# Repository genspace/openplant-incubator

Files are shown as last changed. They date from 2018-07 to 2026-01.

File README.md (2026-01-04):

# OpenPlant Incubator

The code in this repository is open sourced and provides tools to develop a plant incubator.We hope this repository can be used as a model to inspire similar work among other research teams.

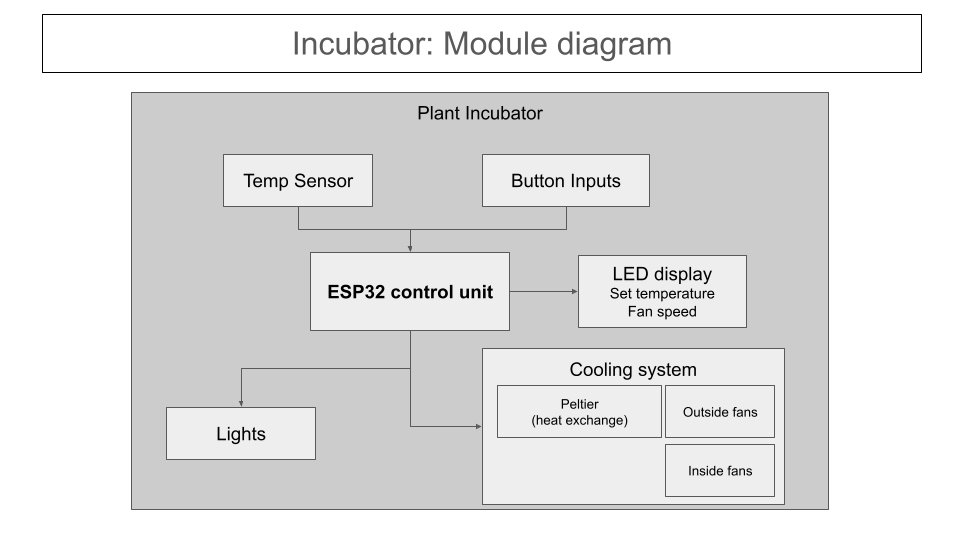
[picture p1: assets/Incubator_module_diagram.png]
Software Schematic


ToDo: Update this https://trello.com/b/W0jccEJs/welcome-to-the-project

Complete block diagram is saved in the genspace/openplant google drive. See `Incubator functional block diagram`

Please feel free to get in touch with the team.

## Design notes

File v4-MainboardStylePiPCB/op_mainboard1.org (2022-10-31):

* Task list [2/2]
- [X] lookup size limitations JLCPCB -- it seems up to 200mm x 200mm would be good
- [X] Schematic [3/3]
  - [X] mosfets
  - [X] I2C
  - [X] ATX
- [X] PCB tasks [12/12]
  - [X] copy shape from PiOnlyPCB V2
  - [X] footprints for 12 pin 3.81mm connectors
  - [X] ATX power distribution
  - [X] ATX power-on switch
  - [X] mosfets
  - [X] I2C
  - no additional copy of RPi header
  - [X] multiple mounting holes with keepouts
  - [X] silk screen additional labels
  - [X] silk screen references
  - [X] edge cuts
  - [X] Open Plant logo / label
  - [X] Flip over RPi connector

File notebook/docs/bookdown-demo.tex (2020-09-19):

\documentclass[]{book}
\usepackage{lmodern}
\usepackage{amssymb,amsmath}
\usepackage{ifxetex,ifluatex}
\usepackage{fixltx2e} % provides \textsubscript
\ifnum 0\ifxetex 1\fi\ifluatex 1\fi=0 % if pdftex
  \usepackage[T1]{fontenc}
  \usepackage[utf8]{inputenc}
\else % if luatex or xelatex
  \ifxetex
    \usepackage{mathspec}
  \else
    \usepackage{fontspec}
  \fi
  \defaultfontfeatures{Ligatures=TeX,Scale=MatchLowercase}
\fi
% use upquote if available, for straight quotes in verbatim environments
\IfFileExists{upquote.sty}{\usepackage{upquote}}{}
% use microtype if available
\IfFileExists{microtype.sty}{%
\usepackage{microtype}
\UseMicrotypeSet[protrusion]{basicmath} % disable protrusion for tt fonts
}{}
\usepackage{hyperref}
\hypersetup{unicode=true,
            pdftitle={A Minimal Book Example},
            pdfauthor={Yihui Xie},
            pdfborder={0 0 0},
            breaklinks=true}
\urlstyle{same}  % don't use monospace font for urls
\usepackage{natbib}
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
\newcommand{\AlertTok}[1]{\textcolor[rgb]{0.94,0.16,0.16}{#1}}
\newcommand{\AnnotationTok}[1]{\textcolor[rgb]{0.56,0.35,0.01}{\textbf{\textit{#1}}}}
\newcommand{\AttributeTok}[1]{\textcolor[rgb]{0.77,0.63,0.00}{#1}}
\newcommand{\BaseNTok}[1]{\textcolor[rgb]{0.00,0.00,0.81}{#1}}
\newcommand{\BuiltInTok}[1]{#1}
\newcommand{\CharTok}[1]{\textcolor[rgb]{0.31,0.60,0.02}{#1}}
\newcommand{\CommentTok}[1]{\textcolor[rgb]{0.56,0.35,0.01}{\textit{#1}}}
\newcommand{\CommentVarTok}[1]{\textcolor[rgb]{0.56,0.35,0.01}{\textbf{\textit{#1}}}}
\newcommand{\ConstantTok}[1]{\textcolor[rgb]{0.00,0.00,0.00}{#1}}
\newcommand{\ControlFlowTok}[1]{\textcolor[rgb]{0.13,0.29,0.53}{\textbf{#1}}}
\newcommand{\DataTypeTok}[1]{\textcolor[rgb]{0.13,0.29,0.53}{#1}}
\newcommand{\DecValTok}[1]{\textcolor[rgb]{0.00,0.00,0.81}{#1}}
\newcommand{\DocumentationTok}[1]{\textcolor[rgb]{0.56,0.35,0.01}{\textbf{\textit{#1}}}}
\newcommand{\ErrorTok}[1]{\textcolor[rgb]{0.64,0.00,0.00}{\textbf{#1}}}
\newcommand{\ExtensionTok}[1]{#1}
\newcommand{\FloatTok}[1]{\textcolor[rgb]{0.00,0.00,0.81}{#1}}
\newcommand{\FunctionTok}[1]{\textcolor[rgb]{0.00,0.00,0.00}{#1}}
\newcommand{\ImportTok}[1]{#1}
\newcommand{\InformationTok}[1]{\textcolor[rgb]{0.56,0.35,0.01}{\textbf{\textit{#1}}}}
\newcommand{\KeywordTok}[1]{\textcolor[rgb]{0.13,0.29,0.53}{\textbf{#1}}}
\newcommand{\NormalTok}[1]{#1}
\newcommand{\OperatorTok}[1]{\textcolor[rgb]{0.81,0.36,0.00}{\textbf{#1}}}
\newcommand{\OtherTok}[1]{\textcolor[rgb]{0.56,0.35,0.01}{#1}}
\newcommand{\PreprocessorTok}[1]{\textcolor[rgb]{0.56,0.35,0.01}{\textit{#1}}}
\newcommand{\RegionMarkerTok}[1]{#1}
\newcommand{\SpecialCharTok}[1]{\textcolor[rgb]{0.00,0.00,0.00}{#1}}
\newcommand{\SpecialStringTok}[1]{\textcolor[rgb]{0.31,0.60,0.02}{#1}}
\newcommand{\StringTok}[1]{\textcolor[rgb]{0.31,0.60,0.02}{#1}}
\newcommand{\VariableTok}[1]{\textcolor[rgb]{0.00,0.00,0.00}{#1}}
\newcommand{\VerbatimStringTok}[1]{\textcolor[rgb]{0.31,0.60,0.02}{#1}}
\newcommand{\WarningTok}[1]{\textcolor[rgb]{0.56,0.35,0.01}{\textbf{\textit{#1}}}}
\usepackage{longtable,booktabs}
\usepackage{graphicx,grffile}
\makeatletter
\def\maxwidth{\ifdim\Gin@nat@width>\linewidth\linewidth\else\Gin@nat@width\fi}
\def\maxheight{\ifdim\Gin@nat@height>\textheight\textheight\else\Gin@nat@height\fi}
\makeatother
% Scale images if necessary, so that they will not overflow the page
% margins by default, and it is still possible to overwrite the defaults
% using explicit options in \includegraphics[width, height, ...]{}
\setkeys{Gin}{width=\maxwidth,height=\maxheight,keepaspectratio}
\IfFileExists{parskip.sty}{%
\usepackage{parskip}
}{% else
\setlength{\parindent}{0pt}
\setlength{\parskip}{6pt plus 2pt minus 1pt}
}
\setlength{\emergencystretch}{3em}  % prevent overfull lines
\providecommand{\tightlist}{%
  \setlength{\itemsep}{0pt}\setlength{\parskip}{0pt}}
\setcounter{secnumdepth}{5}
% Redefines (sub)paragraphs to behave more like sections
\ifx\paragraph\undefined\else
\let\oldparagraph\paragraph
\renewcommand{\paragraph}[1]{\oldparagraph{#1}\mbox{}}
\fi
\ifx\subparagraph\undefined\else
\let\oldsubparagraph\subparagraph
\renewcommand{\subparagraph}[1]{\oldsubparagraph{#1}\mbox{}}
\fi

%%% Use protect on footnotes to avoid problems with footnotes in titles
\let\rmarkdownfootnote\footnote%
\def\footnote{\protect\rmarkdownfootnote}

%%% Change title format to be more compact
\usepackage{titling}

% Create subtitle command for use in maketitle
\providecommand{\subtitle}[1]{
  \posttitle{
    \begin{center}\large#1\end{center}
    }
}

\setlength{\droptitle}{-2em}

  \title{A Minimal Book Example}
    \pretitle{\vspace{\droptitle}\centering\huge}
  \posttitle{\par}
    \author{Yihui Xie}
    \preauthor{\centering\large\emph}
  \postauthor{\par}
      \predate{\centering\large\emph}
  \postdate{\par}
    \date{2019-10-19}

\usepackage{booktabs}
\usepackage{amsthm}
\makeatletter
\def\thm@space@setup{%
  \thm@preskip=8pt plus 2pt minus 4pt
  \thm@postskip=\thm@preskip
}
\makeatother

\begin{document}
\maketitle

{
\setcounter{tocdepth}{1}
\tableofcontents
}
\hypertarget{prerequisites}{%
\chapter{Prerequisites}\label{prerequisites}}

This is a \emph{sample} book written in \textbf{Markdown}. You can use anything that Pandoc's Markdown supports, e.g., a math equation \(a^2 + b^2 = c^2\).

The \textbf{bookdown} package can be installed from CRAN or Github:

\begin{Shaded}
\begin{Highlighting}[]
\KeywordTok{install.packages}\NormalTok{(}\StringTok{"bookdown"}\NormalTok{)}
\CommentTok{# or the development version}
\CommentTok{# devtools::install_github("rstudio/bookdown")}
\end{Highlighting}
\end{Shaded}

Remember each Rmd file contains one and only one chapter, and a chapter is defined by the first-level heading \texttt{\#}.

To compile this example to PDF, you need XeLaTeX. You are recommended to install TinyTeX (which includes XeLaTeX): \url{https://yihui.name/tinytex/}.

\hypertarget{general-use-cases}{%
\chapter{General Use Cases}\label{general-use-cases}}

As a plant researcher, I would like to have an incubator that can be controlled:

\begin{itemize}
\item
  Create schedule for light
\item
  Keep temperature constant
\item
  Keep humidity constant
\end{itemize}

As a plant researcher, I would like to capture periodic data about plants:

\begin{itemize}
\item
  Pictures - once a minute
\item
  Temperature - once a minute
\item
  Humidity - once a minute
\end{itemize}

As a plant researcher, I would like to have the data available in the cloud:

\begin{itemize}
\item
  Store all data on the cloud
\item
  View data in real time on a Web site
\end{itemize}

As a plant researcher, I would like to be able to interact with the incubator in the cloud:

\begin{itemize}
\item
  Receive alerts when the connection is down, or temperature is incorrect
\item
  Ability to change temperature and/or light settings via a Web interface
\end{itemize}

As a plant researcher, I would like to able to use analytics on the data that is captured from the incubator

\hypertarget{raspberry-pi}{%
\chapter{Raspberry Pi}\label{raspberry-pi}}

Flash Raspbian to an SD card.

\begin{itemize}
\item
  Download Raspbian Stretch Lite (raspberry pi operating system image) from \href{https://www.raspberrypi.org/downloads/raspbian/}{here}.
\item
  Download Etcher (a utility which helps you flash an image to an SD card) \href{https://www.balena.io/etcher/}{here}.
\item
  Flash Raspbian on a MicroSD card using Etcher.
\end{itemize}

Enable SSH server before the first boot of the Raspberry Pi.

\begin{itemize}
\item
  View the MicroSD card on your computer.
\item
  Find the ``boot'' partition. Right click and open a terminal.
\item
  Make a file (with nothing in it) called ``ssh'' (no quotes.)
\item
  Add a wpa\_supplicant.conf file (See Appendix A). Copy and paste the file contents from Appendix A
\item
  Change the hostname. (The Raspberry Pi image comprises two partitions. ``root'' and ``boot''. Boot is readable on all operating systems (if you insert the sd card into your laptop or whatever.) Root is only readable on Linux? Maybe Mac?) This can be done in the /rootfs directory. Name your raspberry pi by changing the `hostname' and `hosts'.
\end{itemize}

Boot the Raspbian OS on the Raspberry Pi

\begin{itemize}
\item
  Plug the microSD card into the Pi.
\item
  Power the raspberry pi with a suitable power adapter (or from the computer.)
\item
  Open Terminal. Find the Raspberry Pi on the network. \texttt{ping\ raspberrypi.local} - if it is working, press ctrl c to stop
\item
  Install nmap with \texttt{sudo\ apt\ install\ nmap}. Type: \texttt{sudo\ nmap\ -sP\ 192.168.1.0/24\ \textbar{}\ awk\ \textquotesingle{}/\^{}Nmap/\{ip=\$NF\}/B8:27:EB/\{print\ ip\}\textquotesingle{}} to find the ip address of the Pi.
\end{itemize}

Log into the Pi

\begin{itemize}
\item
  Type \texttt{ssh\ pi@raspberrypi.local} or \texttt{ssh\ pi@\{ip-address\}} where ip-address is the one from the command directly above. Accept the ``host key fingerprint'' which you are told to check. During this step, you are vulnerable to a man-in-the-middle attack. Let's assume that there is no one on the Wi-Fi who is trying to attack you. There are ways to avoid this security hole. (I.e. confirm the host key on the SD card after the first boot, but before you ever log in via SSH.
\item
  Enter the password ``raspberry''. You should change this.
\item
  (New and temporary fix) As per this \href{https://www.techrepublic.com/article/how-to-disable-ipv6-on-linux/}{article}, disable Internet Protocol version 6, as it does not play well with the Genspace Internet Service Provider. Run the following commands in a terminal window:
\end{itemize}

\begin{verbatim}
sudo nano /etc/sysctl.conf
# Add the following three lines to the bottom of the file:
net.ipv6.conf.all.disable_ipv6 = 1
net.ipv6.conf.default.disable_ipv6 = 1
net.ipv6.conf.lo.disable_ipv6 = 1

#Save and close the file.
#Reboot the machine.
\end{verbatim}

\begin{itemize}
\item
  Run \texttt{sudo\ apt-get\ update\ \&\&\ sudo\ apt-get\ -y\ upgrade} to update the system
\item
  run \texttt{sudo\ raspi-config}. In raspi-config turn on the camera and I2C in ``Interfacing Options''. Localization Settings → Keyboard Config → Generic 105 (accept default) → English US → English us → accept all defaults
\item
  Reboot
\item
  Load camera code onto pi.
\item
  Install the picamera library for python: \texttt{sudo\ apt-get\ install\ python3-picamera}
\item
  The code example uses an AWS s3 bucket to upload the files but you can choose whichever service you want.
\end{itemize}

AWS Uploading Notes

\begin{itemize}
\item
  Install the awscli program: \texttt{sudo\ apt-get\ install\ awscli}
\item
  Configure the awscli program: \texttt{aws\ configure}
\end{itemize}

Camera auto-start directions

To make the program start automatically on reboot, I edited the /etc/rc.local file as follows:

\begin{verbatim}
_IP=$(hostname -I) || true
if [ "$_IP" ]; then
  printf "My IP address is %s\n" "$_IP"
fi
su pi -c 'python3 /home/pi/kris_camera.py &'
exit 0
\end{verbatim}

\textbf{Fill In Code For Connecting Arduino And Serial Script}

\hypertarget{the-container}{%
\chapter{The Container}\label{the-container}}

Notes

\begin{itemize}
\tightlist
\item
  Designed for both Petri and `square dishes' - 4 dishes
\item
  29cm wide interior
\item
  35cm long interior
\item
  20cm high
\item
  Petri dishes are 9cm in diameter
\item
  Square dishes are 10.2cm on four sides, and 7.49cm high
\item
  Peltier+ device is 5+ cm both inside and outside
\end{itemize}

BRING LIST
* Duct tape
* Box corners
* Popsicle sticks
* Electrical tape
* Scissors
* Foam core (0.25 inch thick)
* Box cutter and or pocket knife

Polystyrene - 6 pieces and maybe some extra
* Bottom is longer in both directions
* Longer side is longer
* Shorter side is the same

Electronics
* List is on github
* Waldo has many items
* Kris to order lights

The picture is below. The desired measurements details are as follows:

20cm by 29cm by 35cm
If building, the bottom/top should longer in both directions. So, if the polystyrene is one inch thick, this means the bottom should be 2 inches (or 5+cm) longer in each dimension.
The longer two side panels should be 2 inches (or 5+cm) longer in just the length
The shorter two side panels should not have any additions
So
2 x (34 x 40cm)
2 x (20cm x 40cm)
2 x (20cm by 29 cm)

\hypertarget{arduino}{%
\chapter{Arduino}\label{arduino}}

The layout for the Arduino. What you need:

\begin{itemize}
\item
  Arduino (Uno)
\item
  \href{https://cdn.sparkfun.com/datasheets/Components/General/FQP30N06L.pdf}{Mosfet} x 2
\item
\end{itemize}

Check the code (incubator\_main.ino in \url{https://github.com/genspace/openplant-incubator}) for which pins on the Arduino to connect the lights and Peltier to. As of 10/12/19, the lights go to pin 4 and the Peltier goes to pin 5.

The Mosfet, I think it's the one above, or the one in the link below. You can always to a Google search on the.
\url{https://cdn.sparkfun.com/datasheets/Components/General/FQP30N06L.pdf}

The Peltier Module TEC1-12706
\url{https://www.electron.com/media/389/datasheet-601-017.pdf?\&key=ZGpmIyQwNUZfMzg5}

Wire the Temperature/Humidity sensor (SHT31) according to this diagram:

Fan Wiring:
We don't need to wire Sense or Control because we leave the fans always on.
\url{https://allpinouts.org/pinouts/connectors/motherboards/motherboard-cpu-4-pin-fan/}

Real Time Clock wiring
GND to GND on your board
VCC to the logic level power of your board (on classic Arduinos \& Metros use 5V, on 3.3V devices use 3.3V)
SDA to the SDA i2c data pin (A4)
SCL to the SCL i2c clock pin (A5)

\url{https://learn.adafruit.com/adafruit-pcf8523-real-time-clock/rtc-with-arduino}
\url{https://learn.adafruit.com/adafruit-metro-mini/pinouts}
Set the time by running the example script: \url{https://github.com/adafruit/RTClib/blob/master/examples/pcf8523/pcf8523.ino}

Power Supply goes into the rails -- black into one, and red into another..

Uploading code into an Arduino (in our case the Adafruit Metro Mini, which is equivalent to the Arduino Uno.)

Install the Arduino IDE

Open the IDE. (This gives a blank document. Just ``setup()'' and ``loop()'' functions

Select the board. (In tools?)

Select the serial device which you're using. (Windows? COM1 ?)

Lots of restarting if the serial port is not found.

Open a (second) window using File → Examples → Basic(?) → Blink

Build and upload buttons are the check mark and the arrow, respectively

\hypertarget{final-words}{%
\chapter{Final Words}\label{final-words}}

We have finished a nice book.

Raspberry Pi Onboard LEDs: \href{https://raspberrypi.stackexchange.com/questions/44168/how-can-i-control-the-red-led-again/61955\#61955}{Guide}

\begin{verbatim}
sudo sh -c "echo none > /sys/class/leds/led0/trigger"         # Static LED off 
sudo sh -c "echo default-on > /sys/class/leds/led0/trigger"   # Static LED on 
sudo sh -c "echo mmc0 > /sys/class/leds/led0/trigger"         # The normal behaviour
\end{verbatim}

Appendix A

Configuring what WiFi access point the Raspberry Pi will connect to before booting it for the first time. (This way, you don't need a monitor and keyboard to configure the Pi.)
Put the ``ssh'' file (empty) in the ``boot'' partition of the SD card. (Already mentioned in the main steps.)
Put this in a text file named ``wpa\_supplicant.conf'' in the ``boot'' partition of the SD card.

\begin{verbatim}
country=US
ctrl_interface=DIR=/var/run/wpa_supplicant GROUP=netdev
update_config=1

network={
    ssid="Genspace"
    scan_ssid=1
    psk="Microbes"
    key_mgmt=WPA-PSK
}
\end{verbatim}

Additional Raspberry Pi Notes

auto re-start

\$ su pi -c `python3 /home/pi/kris\_camera.py \&'

Alternatively, this can be done with the `pi' user's crontab.

Camera / Tongue Depressor measurements:

The Camera should be inches from bottom. (Let's say 6 or 7 inches)
Square easier than round. Exacto-type knife is better than drilling for tongue depressors.
The camera has a lens holder that is circular -- 0.289 inches in diameter
The square pieces that holds the camera is 0.336 inches in diameter.

Check this link for camera resolution: \url{https://picamera.readthedocs.io/en/release-1.12/fov.html}

\bibliography{book.bib,packages.bib}

\end{document}

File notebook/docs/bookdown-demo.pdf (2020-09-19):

# A Minimal Book Example

### Yihui Xie

2019-10-19

2

# Contents

1 Prerequisites | 5
2 General Use Cases | 7
3 Raspberry Pi | 9
4 The Container | 13
5 Arduino | 15
6 Final Words | 17

3

4 | CONTENTS

# Chapter 1

# Prerequisites

This is a sample book written in Markdown. You can use anything that Pandoc’s Markdown supports, e.g., a math equation a

2 + b

2 = c

2

The bookdown package can be installed from CRAN or Github: install.packages("bookdown")
# or the development version

# devtools::install_github("rstudio/bookdown")

Remember each Rmd file contains one and only one chapter, and a chapter is defined by the first-level heading #.

To compile this example to PDF, you need XeLaTeX. You are recommended to install TinyTeX (which includes XeLaTeX): https://yihui.name/tinytex/.

5

6 | CHAPTER 1. PREREQUISITES

# Chapter 2

# General Use Cases

As a plant researcher, I would like to have an incubator that can be controlled:

- Create schedule for light
- Keep temperature constant
- Keep humidity constant

As a plant researcher, I would like to capture periodic data about plants:

- Pictures - once a minute
- Temperature - once a minute
- Humidity - once a minute

As a plant researcher, I would like to have the data available in the cloud:

- Store all data on the cloud
- View data in real time on a Web site

As a plant researcher, I would like to be able to interact with the incubator in the cloud:

- Receive alerts when the connection is down, or temperature is incorrect
- Ability to change temperature and/or light settings via a Web interface

As a plant researcher, I would like to able to use analytics on the data that is captured from the incubator

7

8 | CHAPTER 2. GENERAL USE CASES

# Chapter 3

# Raspberry Pi

Flash Raspbian to an SD card.

- Download Raspbian Stretch Lite (raspberry pi operating system image) from here. (https://www.raspberrypi.org/downloads/raspbian/)
- Download Etcher (a utility which helps you flash an image to an SD card) here. (https://www.balena.io/etcher/)
- Flash Raspbian on a MicroSD card using Etcher.

Enable SSH server before the first boot of the Raspberry Pi.

- View the MicroSD card on your computer.
- Find the “boot” partition. Right click and open a terminal.
- Make a file (with nothing in it) called “ssh” (no quotes.)
- Add a wpa_supplicant.conf file (See Appendix A). Copy and paste the file contents from Appendix A
- Change the hostname. (The Raspberry Pi image comprises two partitions. “root” and “boot”. Boot is readable on all operating systems (if you insert the sd card into your laptop or whatever.) Root is only readable on Linux? Maybe Mac?) This can be done in the /rootfs directory. Name your raspberry pi by changing the ‘hostname’ and ‘hosts’.

Boot the Raspbian OS on the Raspberry Pi

- Plug the microSD card into the Pi.
- Power the raspberry pi with a suitable power adapter (or from the computer.)
- Open Terminal. | Find the Raspberry Pi on the network. | ping
raspberrypi.local - if it is working, press ctrl c to stop
| 9

10 | CHAPTER 3. RASPBERRY PI
- Install nmap with sudo apt install nmap. | Type: sudo nmap -sP
192.168.1.0/24 | awk '/^Nmap/{ip=$NF}/B8:27:EB/{print ip}' to
find the ip address of the Pi.

Log into the Pi

- Type ssh pi@raspberrypi.local or ssh pi@{ip-address} where ip-address is the one from the command directly above. Accept the “host key fingerprint” which you are told to check. During this step, you are vulnerable to a man-in-the-middle attack. Let’s assume that there is no one on the Wi-Fi who is trying to attack you. There are ways to avoid this security hole. (I.e. confirm the host key on the SD card after the first boot, but before you ever log in via SSH.
- Enter the password “raspberry”. You should change this.
- (New and temporary fix) As per this article, (https://www.techrepublic.com/article/how-to-disable-ipv6-on-linux/) disable Internet Protocol version 6, as it does not play well with the Genspace Internet Service Provider. Run the following commands in a terminal window:

sudo nano /etc/sysctl.conf
# Add the following three lines to the bottom of the file: net.ipv6.conf.all.disable_ipv6 = 1 net.ipv6.conf.default.disable_ipv6 = 1 net.ipv6.conf.lo.disable_ipv6 = 1

#Save and close the file.

#Reboot the machine.

- Run sudo apt-get update && sudo apt-get -y upgrade to update the system
- run sudo raspi-config. In raspi-config turn on the camera and I2C in “Interfacing Options”. Localization Settings → Keyboard Config → Generic 105 (accept default) → English US → English us → accept all defaults
- Reboot
- Load camera code onto pi.
- Install the picamera library for python: sudo apt-get install python3-picamera
- The code example uses an AWS s3 bucket to upload the files but you can choose whichever service you want.

AWS Uploading Notes

- Install the awscli program: sudo apt-get install awscli
- Configure the awscli program: aws configure

11

Camera auto-start directions

To make the program start automatically on reboot, I edited the /etc/rc.local file as follows:

_IP=$(hostname -I) || true
if [ "$_IP" ]; then
printf "My IP address is %s\n" "$_IP"
fi
su pi -c 'python3 /home/pi/kris_camera.py &'
exit 0

Fill In Code For Connecting Arduino And Serial Script

12 | CHAPTER 3. RASPBERRY PI

# Chapter 4

# The Container

Notes

- Designed for both Petri and ‘square dishes’ - 4 dishes
- 29cm wide interior
- 35cm long interior
- 20cm high
- Petri dishes are 9cm in diameter
- Square dishes are 10.2cm on four sides, and 7.49cm high
- Peltier+ device is 5+ cm both inside and outside

BRING LIST * Duct tape * Box corners * Popsicle sticks * Electrical tape * Scissors * Foam core (0.25 inch thick) * Box cutter and or pocket knife

Polystyrene - 6 pieces and maybe some extra * Bottom is longer in both directions * Longer side is longer * Shorter side is the same

Electronics * List is on github * Waldo has many items * Kris to order lights

The picture is below. The desired measurements details are as follows:

20cm by 29cm by 35cm If building, the bottom/top should longer in both directions. So, if the polystyrene is one inch thick, this means the bottom should be 2 inches (or 5+cm) longer in each dimension. The longer two side panels should be 2 inches (or 5+cm) longer in just the length The shorter two side panels should not have any additions So 2 x (34 x 40cm) 2 x (20cm x 40cm) 2 x (20cm by 29 cm)

13

14 | CHAPTER 4. THE CONTAINER

# Chapter 5

# Arduino

The layout for the Arduino. What you need:

- Arduino (Uno)
- Mosfet (https://cdn.sparkfun.com/datasheets/Components/General/FQP30N06L.pdf) x 2

•

Check the code (incubator_main.ino in https://github.com/genspace/openplant-incubator) (https://github.com/genspace/openplant-incubator) for which pins on the Arduino to connect the lights and Peltier to. As of 10/12/19, the lights go to pin 4 and the Peltier goes to pin 5.

The Mosfet, I think it’s the one above, or the one in the link below. You can always to a Google search on the. https://cdn.sparkfun.com/datasheets/Components/General/FQP30N06L.pdf (https://cdn.sparkfun.com/datasheets/Components/General/FQP30N06L.pdf)

The Peltier Module TEC1-12706 https://www.electron.com/media/389/datasheet-601-017.pdf?&key=ZGpmIyQwNUZfMzg5 (https://www.electron.com/media/389/datasheet-601-017.pdf?&key=ZGpmIyQwNUZfMzg5)

Wire the Temperature/Humidity sensor (SHT31) according to this diagram:

Fan Wiring: We don’t need to wire Sense or Control because we leave the fans always on. https://allpinouts.org/pinouts/connectors/motherboards/motherboard-cpu-4-pin-fan/ (https://allpinouts.org/pinouts/connectors/motherboards/motherboard-cpu-4-pin-fan/)

Real Time Clock wiring GND to GND on your board VCC to the logic level power of your board (on classic Arduinos & Metros use 5V, on 3.3V devices use 3.3V) SDA to the SDA i2c data pin (A4) SCL to the SCL i2c clock pin (A5)

https://learn.adafruit.com/adafruit-pcf8523-real-time-clock/rtc-with-arduinohttps://learn.adafruit.com/adafruit-metro-mini/pinouts Set the time by running the example script: https://github.com/adafruit/RTClib/blob/master/examples/pcf8523/pcf8523.ino (https://github.com/adafruit/RTClib/blob/master/examples/pcf8523/pcf8523.ino)

Power Supply goes into the rails – black into one, and red into another..

| 15

16 | CHAPTER 5. ARDUINO

Uploading code into an Arduino (in our case the Adafruit Metro Mini, which is equivalent to the Arduino Uno.)

Install the Arduino IDE

Open the IDE. (This gives a blank document. Just “setup()” and “loop()” functions

Select the board. (In tools?)

Select the serial device which you’re using. (Windows? COM1 ?)

Lots of restarting if the serial port is not found.

Open a (second) window using File → Examples → Basic(?) → Blink

Build and upload buttons are the check mark and the arrow, respectively

# Chapter 6

# Final Words

We have finished a nice book.

Raspberry Pi Onboard LEDs: Guide (https://raspberrypi.stackexchange.com/questions/44168/how-can-i-control-the-red-led-again/61955)

sudo sh -c "echo none > /sys/class/leds/led0/trigger" | # Static LED off
sudo sh -c "echo default-on > /sys/class/leds/led0/trigger" | # Static LED on
sudo sh -c "echo mmc0 > /sys/class/leds/led0/trigger" | # The normal behaviour

Appendix A

Configuring what WiFi access point the Raspberry Pi will connect to before
booting it for the first time. (This way, you don’t need a monitor and keyboard
to configure the Pi.) Put the “ssh” file (empty) in the “boot” partition of the SD card. (Already mentioned in the main steps.) Put this in a text file named “wpa_supplicant.conf” in the “boot” partition of the SD card.

country=US
ctrl_interface=DIR=/var/run/wpa_supplicant GROUP=netdev update_config=1

network={
ssid="Genspace"
scan_ssid=1
psk="Microbes"
key_mgmt=WPA-PSK
}

Additional Raspberry Pi Notes

auto re-start

$ su pi -c ‘python3 /home/pi/kris_camera.py &’

Alternatively, this can be done with the ‘pi’ user’s crontab.

17

18 | CHAPTER 6. FINAL WORDS

Camera / Tongue Depressor measurements:

The Camera should be inches from bottom. (Let’s say 6 or 7 inches) Square easier than round. Exacto-type knife is better than drilling for tongue depressors. The camera has a lens holder that is circular – 0.289 inches in diameter The square pieces that holds the camera is 0.336 inches in diameter.

Check this link for camera resolution: https://picamera.readthedocs.io/en/release-1.12/fov.html (https://picamera.readthedocs.io/en/release-1.12/fov.html)

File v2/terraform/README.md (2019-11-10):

# OpenPlant Infra

This repo contains the code necessary to spin up AWS infrastructure relevant to OpenPlant App.
Currently, it includes instructions to create an Ubuntu EC2 Server.

## How To

In order to use this repo, the user must take the following steps on their system:

1. Install [terraform]
2. Create a file in project root called `secret.tfvars` with the following contents:

>```
>access_key = "<YOUR AWS ACCESS KEY>"
>secret_key = "<YOUR AWS SECRET KEY>"
>ssh_key_name = "<RSA KEY FILE NAME>"
>ssh_key_pub = "<PUBLIC RSA KEY CONTENTS>"
>```

1. Now, run `terraform init` in the project directory to initialize terraform access
2. Simply call `./bin/do.sh apply` in the project root to create infrastructure

[terraform]: https://www.terraform.io/downloads.html

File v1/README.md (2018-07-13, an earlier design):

# OpenPlant Incubator

This project is to support the creation of an inexpensive plant incubator for the growth of liveworts (_Marchantia polymorpha_) which is the model system used by the [OpenPlant][1] collaboration. Our hope is that this design will allow a diverse array of (citizen) scientists cultivate plants under controlled conditions and potentially contribute to basic research.

## Incubator design

This design attempts to replicate the ideal conditions identified by Vujičić ([et al. 2010][2]) and reported by Chiyoda ([et al. 2008][3]). These conditions can be summarized as:

* 22°C
* 50-60 μmol photons/m<sup>2</sup>s (which for cool white fluorescent light equals 3700-4440 lux \[[Thimijan and Heins 1983][4]\])
* 16 h light, 8 h dark cycle

Furthermore we would like this project to be a relatively simple build so in general we are using well documented components from [Adafruit][5]. However the use of a wide array of purchased or scavenged parts is encouraged. We will describe the parts and their interaction with code in the "Description of parts" section, so jump there if you're trying to make a substitution(s).

## Description of files

What follows is a description of the code used in this project. We recommend branches (and forks) to incorporate alternate hardware. The raspberry_pi branch is currently in development to incorporate remote monitoring by reading off the data the microcontroller sends out via USB serial connection.

* **Test_data**

	This folder contains a collection of .LOG files which are CSV output from the incubator logs collected over a few days at Genspace. I did a rough visualization the data using the R script "data_cleanup.R". The report "data_cleanup.html" can be generated by running the script "report_generation.R".

* **initialization**

	This folder contains an unfinished Arduino script which is intended to be run to set up the incubator.

* **prototype_incubator**

	This folder contains the code for the incubator. Please consult the source code for inline comments describing it's operation.

* **unit_tests**

	This folder contains a group of scripts which for the most part are just slightly modified example code from various tutorials which test each component of the incubator to ensure they are operating correctly. Code should be run and then the physical device inspected and perturbed to troubleshoot issues as they arise. A multimeter will be very useful in this process.

* **liverwort_incubator_v1.fzz**

	This fritzing diagram contains the plan for the incubator electronics as it is assembled for the working prototype. Please consider this the build guide recognizing that there are many issues of physical connection which cannot be captured in such a diagram.

* **prototype_breadbaord.fzz**

	This fritzing diagram contains the plan for the incubator electronics as it was planned out on a breadboard. It's not the most up to date and should be taken with a grain of salt.

## Description of parts

What follows is a list of parts with links to either the part I used in the project build or an example of the part. Please reference the fritzing diagrams (see the previous section) for the exact build of the incubator.

### Major components

These are parts which form the bulk of the incubator which you likely will have to source from the internet unless you have some expertise in salvage or great local hobby/junk shops.

* **Micro-controller**, [Metro Mini][7]

	Uses an ATmega328 based microcontroller like the Arduino UNO. We chose this particular board because it has many GPIO pins and it fits nicely into a breadboard for when I was prototyping.The USB support allows is to easily program it over USB and send data out via this connection. It's also important that it has a 5V regulator to power the sensors. It can also deliver 3.3V regulated which allows for a more diverse array of breakout modules to be used. I'm also controlling the fans using the "blue" PWM wire which is specified at 24kHz which can be achieved by modifying the internal registers (see the code).

* **Real time clock**, [PCF8523][8]

	This was the cheapest I2C RTC breakout module on Adafruit. It is required to timestamp the data being written to the logs. We think logs are the best way to ensure experiments are conducted under controlled conditions as well as to ensure the incubator is properly working. One could also imagine that a small computer (like a pi) could also serve this function if always connected by serial. The I2C standard allows this to easily share a bus with other sensors as long as there are no address collisions.

* **SD card**, [MicroSD breakout board][9]

	With the RTC this forms the basis of the data logging functionality. SD cards use 3.3V logic so depending on the hardware that used you may have to add in a voltage regulator. This particular board from Adafruit can shift 5V to 3.3V so it can share a power bus with the rest of the breakout modules used in this project.

* **Temperature sensor**, [SHT31-D][10]

	This temperature sensor can also record humidity and operates over the I2C bus. It can be powered by 5V or 3.3V. The better the resolution of this device the better the output of the peltiers can be modified to maintain the setpoint temperature. However this is also limited by the sampling frequency.

* **Light sensor**, [TSL2561][11]

	This light sensor operates over the I2C bus as the other sensors in this project do and has an onboard voltage regulator allowing it to receive 5V (it operated on 3.3V).

* **N-channel MOSFET**, [IRLB8721][19]

	A transistor component was chosen to regulate the 12V power source to the LEDs and the peltier using the PWM control from the micro-controller. This could probably be substituted with a variety of components. We used an N-channel MOSFET here because it was what we were most comfortable with. It's important it can block 12V, responds to 5V (or low current) and about 6A per peltier used. Also make sure to stick a heat sink on it.

* **Peltier**, [TEC1-12706][12]

	Peltier elements use electrical energy to pump heat across their body. This results in one hot side and one cold side. This particular module uses 12V which works with the 12V fans off a common power bus. Together with the CPU fan/heatskinks, thermal paste, craft foam and screws they are assembled into units which much be installed into the walls of the incubator.

* **Fan and heatsink**, [CPU cooler][13]

	I didn't purchase this part from a store. Instead I was able to get many of these inexpensively off of Craigslist. I have also seen them on eBay for cheap. CPU fans have 4-pin connections which conform to standard [specifications][14]. Briefly, 12V and ground make up two pins. The third is for fan speed control and accepts a 24kHz PWM signal and the fourth is the output of Hall-effect sensors which measure RPM. 3-pin fans will have to be controlled by a transistor modulating the 12V via PWM from the micro-controller. If possible get fans which have mounting holes which do not align with the heatsink block. This is because these holes will be used to thread a screw to the mounting holes of another fan and heatsink sandwiching the peltier and craft foam in between. If holes align with the heatsink the screws will have to pass through the heatsink in order to reach the opposite mounting holes. Two (near) identical fans with heat sinks will be required per peltier. In the example of this Intel brand stock fan, I cut out the plastic mounting hardware leaving only the holes so that I could used screws for the assembly.

* **LED**, [7020 rigid strip][15]

	This product was chosen because it emits cool white light which is most similar to the cool white fluorescent light which is described in the literature on growth conditions. It uses a maximum of 12V which can be modulated lower to adjust the brightness. Furthermore, it was already mounted on an adhesive backed heatsink which would make installation easier in the incubator.

* **Diffuser**, [Diffuser film][16]

	This is another product which I did not purchase. Instead I was able to salvage the backlight diffuser from inside an LED television. It was gloss on one side and matte on the other. I liked this solution because it was stiff enough to remain an even layer which could be supported by push pins into short pieces of wood dowling which was glued to the lid of the incubator. A great alternative which I tested was inexpensive [white plastic table cloth][17]. In this case it is light enough to be supported by paper clips or similar flexible wire. It won't lie as an even layer, but this minimally affects the variance in light intensity.

* **Voltage shifter**, [MP1584EN][18]

	This breakout is a buck DC-DC voltage converter which works to step down voltage using high frequency switching. In this design it is useful because it has a potentiometer which controls the final output voltage allowing me to manually set the brightness of the LED light source in the hardware. It also shares some of the thermal load of voltage step down from the 12V source with the voltage regulator on the micro-controller board. A maximum of 3A can pass through this module. I'm not sure if this is really required in he final build as presumably the 12V can be directly regulated on the micro-controller board and the transistor which controls the LEDs can be fed a PWM signal which corresponds to the desired light level. Also please note how awkwardly spaced the pins are on this board so you have to solder headers on kinda crooked to fit into a breadboard/perfboard.

* **Power supply**, [12V 360W Switching][20]

	I did not purchase this on Amazon. I was able to find a deal for this device on Craigslist and this seems like the item that I purchased. Many options exist here as long as they have enough power to drive everything. According to some very rough calculations I think the incubator as I built version 1 uses about 108W (it might be less). An ATX (desktop computer) power supply could also be used as it provides both 12V and 5V. That would remove another reason to use a buck external voltage shifter. 

* **Insulated chamber**, [Styrofoam box][21]

	Walk around the city and I'm sure you will find one of these kicking about. The thicker the walls the better the insulation but also the more difficult it will be to cut holes to mount your fan-heatsink-peltier-heatskink-fan constructions. I found mine outside of a grocery store and it was previously used to transport fish. I've also spotted them outside of clinics (for pharmaceutical transport). The flatter the better because this design wants to minimize the distance between the plants and the lights to decrease the amount of energy needed to achieve a particular luminous intensity. A layered design could be explored but keep in mind that the more LED strips are added (and the harder they work) the more cooling is required during the light cycle.

### Little things

The following items were sourced from various local stores (except for the wire wrapping supplies and headers) and links are only provided as examples of these items. They represent the smaller items which bind the whole project together. In general, they don't warrant too much discussion.

* **Resistors**, [10K][29]
* **Craft foam**, [any colour!][22]
* **Thermal paste**, [tub][23]
* **Dowling**, [1/4 inch: wood][24]
* **Screws**, [M2 + M3 with nuts and washers][25]
* **Connectors**, Jumper wire crimp connectors: [male][26]; [female][27]; [Stacking headers][28]
* **Wire wrap**, [30AWG][30]
* **Wrap tool**, [HSM30][31]

	 I chose to assemble the project with minimal solder (only using it to join wires when required). This was because of an earlier frustration making solder bridges and keeping the possibility open of taking apart the board for repairs or upgrade. I used a [wire wrap][33] technique to connect components on the board and for components off the board I used wires with male or female crimp connectors which could connect to headers (on the board or on the component itself).

* **Perf board**, [22 x 26][32]

	 You could also use ones with pads connecting the holes and then use solder to connect components instead of wire wrap

## Future development

Some ideas and priorities for future work on this project:

1. Protect the circuit from failure with some capacitors and diodes to prevent back voltages and spikes.
	* I notice that when the fans get touched (and the inductive load slowed) the clock time gets messed up.

2. Definitively decide if the PID parameters are properly tuned.

3. Develop remote monitoring and remote parameter adjustment.

4. Introduce heating control via an H-bridge to switch the voltage polarity on the peliters.
	* I was originally going to use cheap [motor drivers][6] from Amazon, but the peltiers use more current than they are rated for.

5. Complete an initialization script which incorporates unit tests.

6. Rewrite the code as a state based machine (using the millis() function) to allow for different sensor polling times and better interrupt handling.

[1]: https://www.openplant.org/ (openplant homepage)
[2]: http://www.pmf.kg.ac.rs/kjs/volumes/kjs32/kjs32vujiciccvetic73.pdf (vujicic paper)
[3]: https:/dx.doi.org/10.1007/s00299-008-0570-5 (chiyoda paper)
[4]: http://agris.fao.org/agris-search/search.do?recordID=US19850000983 (thimijan paper)
[5]: https://www.adafruit.com/ (adafruit homepage)
[6]: https://www.amazon.com/gp/product/B077P1D41F (motor drivers)
[7]: https://www.adafruit.com/product/2590 (metro mini)
[8]: https://www.adafruit.com/product/3295 (PCF8523)
[9]: https://www.adafruit.com/product/254 (SD breakout)
[10]: https://www.adafruit.com/product/2857 (SHT31-D)
[11]: https://www.adafruit.com/product/439 (TSL2561)
[12]: https://www.amazon.com/Glamorway-TEC1-12706-Thermoelectric-Cooling-Peltier/dp/B00IKDL22O/ (TEC1-12706)
[13]: https://www.amazon.com/Intel-LGA115x-CPU-Heatsink-E97379-003/dp/B01MSD39CN (Intel stock)
[14]: http://www.formfactors.org/developer%5Cspecs%5CREV1_2_Public.pdf (4-pin fan)
[15]: https://www.amazon.com/gp/product/B00NFBG1O0/ (7020 LED)
[16]: https://www.inventables.com/technologies/light-diffuser-film-rolls (diffuser film)
[17]: https://www.dollartree.com/White-Plastic-Tablecovers/p61986/index.pro (table cloth)
[18]: https://www.amazon.com/gp/product/B01MQGMOKI/ (MP1584EN)
[19]: https://www.adafruit.com/product/355 (IRLB8721)
[20]: https://www.amazon.com/dp/B06VWV5YCH/ref=psdc_1161760_t1_B01EWG6YT8 (power supply)
[21]: https://www.mrboxonline.com/16375x115x6-quart-styrofoam-cooler-p-47940.html (box)
[22]: https://www.michaels.com/12x18-foam-sheet-by-creatology/M10597609.html (craft foam)
[23]: https://www.newegg.com/Product/Product.aspx?Item=N82E16835103080 (thermal paste)
[24]: https://www.homedepot.com/p/Builder-s-Choice-1-4-in-x-36-in-Oak-Round-Dowel-HDDO1436/206184687 (dowling)
[25]: https://www.homedepot.com/p/Everbilt-Zinc-Plated-Machine-Screw-Kit-405-Piece-803264/205949025 (screws)
[26]: https://tinkersphere.com/breadboard-perfboard-prototyping/2309-male-jumper-wire-crimp-connector-for-breadboards-10-pack.html (male breadboard crimp connectors)
[27]: https://tinkersphere.com/breadboard-perfboard-prototyping/1562-female-jumper-wire-crimp-connector-for-breadboards-10-pack.html (matching female crimp connectors)
[28]: https://www.sparkfun.com/products/10007 (stacking headers)
[29]: https://www.adafruit.com/product/2784 (10K resistors)
[30]: https://www.jameco.com/z/901-0-Wire-Wrap-Kynar-Black-100-Feet-30AWG-100-Foot-Rolls-_22577.html (wire wrap)
[31]: https://www.jameco.com/z/HSM30-JDV-Products-Strip-Wrap-Unwrap-Tool_34585.html?CID=MERCH (wire wrap tool)
[32]: https://www.allelectronics.com/category/455/perf-boards/1.html (perf board)
[33]: https://makezine.com/2009/07/27/lost-knowledge-wire-wrapping/ (wire wrap)

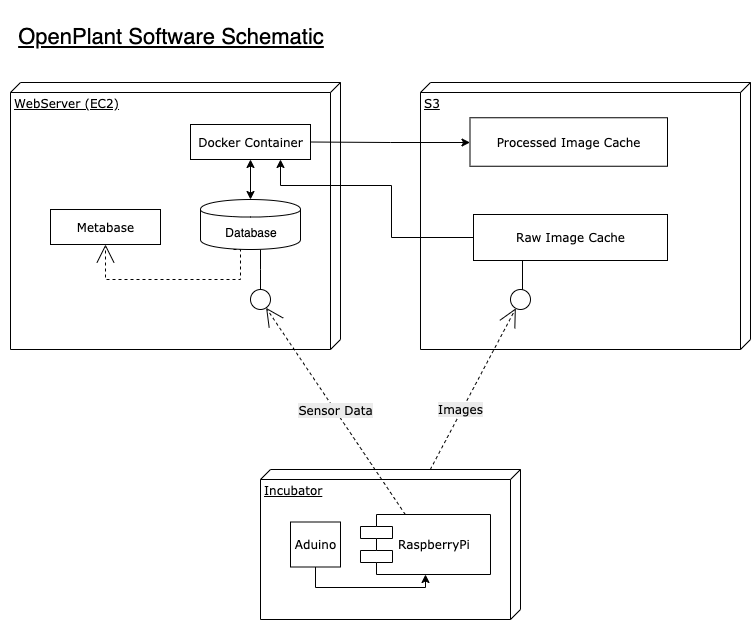
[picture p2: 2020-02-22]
assets/software_schematic.png

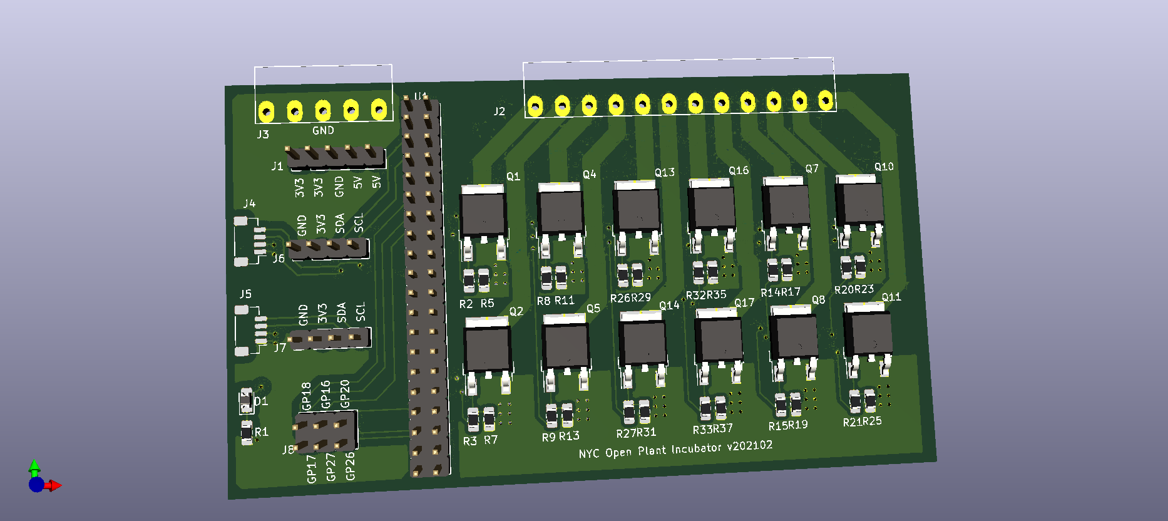
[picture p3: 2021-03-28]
v3-PiOnlyPCB/v202102/v202102_incubator_pcb_3d.png

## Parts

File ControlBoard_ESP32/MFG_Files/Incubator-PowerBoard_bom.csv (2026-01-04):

Component | Description | Part | References | Quantity Per PCB | Datasheet | Value | Footprint | MPN | Digikey_Part_Number
1 | ATX Power supply 24pins | ATX-24 | J13 | 1 | https://www.intel.com/content/dam/www/public/us/en/documents/guides/power-supply-design-guide-june.pdf | ATX-24 | Molex_Mini-Fit_Jr_5569-24A2_2x12_P4.20mm_Horizontal
2 | CONN HDR 12POS 0.1 TIN PCB | Conn_01x12_Socket | J1 | 1 | https://mm.digikey.com/Volume0/opasdata/d220001/medias/docus/937/Female_Headers.100_DS.pdf | Conn_01x12_Socket | PinSocket_1x12_P2.54mm_Vertical | PPTC121LFBN-RC | S6100-ND
3 | CONN HDR 16POS 0.1 TIN PCB | Conn_01x16_Socket | J2 | 1 | https://mm.digikey.com/Volume0/opasdata/d220001/medias/docus/937/Female_Headers.100_DS.pdf | Conn_01x16_Socket | PinSocket_1x16_P2.54mm_Vertical | PPTC161LFBN-RC | S7014-ND
4 | Generic connector, double row, 02x10, odd/even pin numbering scheme (row 1 odd numbers, row 2 even numbers), script generated (kicad-library-utils/schlib/autogen/connector/) | Conn_02x10_Odd_Even | J11 | 1 | ~ | Conn_02x10_Odd_Even | PinHeader_2x10_P2.54mm_Vertical
5 | CONN HEADER VERT 4POS 2.54MM | Conn_01x04_Pin | J3 J4 J5 J6 J10 | 5 | https://www.we-online.com/components/products/datasheet/61300411121.pdf | OUT_FAN_1 | PinHeader_1x04_P2.54mm_Vertical | 61300411121 | 732-5317-ND
6 | CONN HEADER VERT 2POS 2.54MM | Conn_01x02_Pin | J8 J9 J12 | 3 | https://www.we-online.com/components/products/datasheet/61300211121.pdf | PELTIER_1 | PinHeader_1x02_P2.54mm_Vertical | 61300211121 | 732-5315-ND
7 | MOSFET N-CH 30V 6A TSOT26 | 2N7002E_1 | Q1 Q2 Q3 Q4 Q5 | 5 | https://www.diodes.com/assets/Datasheets/DMG6402LVT.pdf | OUT_FAN_1 | SOT-23-6 | DMG6402LVT-7 | DMG6402LVT-7DICT-ND
8 | RES 0 OHM JUMPER 1/10W 0603 | R_US | R6 R7 R8 | 3 | https://www.seielect.com/catalog/sei-rmcf_rmcp.pdf | 0R | R_0603_1608Metric | RMCF0603ZT0R00 | RMCF0603ZT0R00CT-ND
9 | Thick Film Resistors CRCW1210-IF 200 1K0 5% ET1 E3 | R_US | R1 R2 | 2 | https://www.vishay.com/doc?20024 | 1K | R_1210_3225Metric | CRCW12101K00JNEAIF
10 | RES 10K OHM 5% 1/10W 0603 | R_US | R3 R4 R5 | 3 | https://www.seielect.com/catalog/sei-rmcf_rmcp.pdf | 10K | R_0603_1608Metric | RMCF0603JT10K0 | RMCF0603JT10K0CT-ND
Component Groups: | 12
Component Count: | 30
Fitted Components: | 25
Number of PCBs: | 1
Total components: | 25
Schematic Version: | v01a
Schematic Date: | 2024-07-20
PCB Variant: | default
BoM Date: | 2024-11-21T12:36:54-0500
Schematic Source: | Incubator-PowerBoard.kicad_sch
KiCad Version: | Eeschema 8.0.2

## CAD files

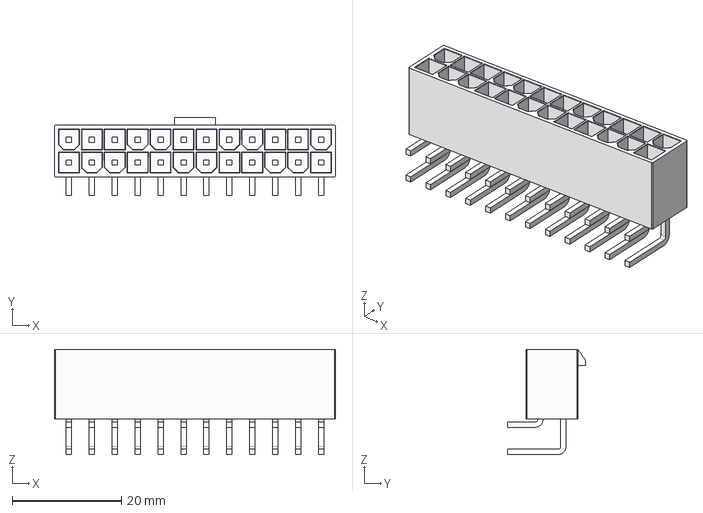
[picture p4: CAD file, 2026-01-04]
ControlBoard_ESP32/3d/ATX_Connector_24pi_90deg.stp
51.5 x 14.3 x 19.3 mm

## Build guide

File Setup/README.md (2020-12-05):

# <ins>Raspberry Pi Setup Guide</ins>
### Written for [Genspace's Open Plant Community Project](https://www.genspace.org/community-projects)

  The goal of this guide is to create a minimal equipment, lowest-cost setup possible for a Raspberry Pi (including associated peripherals) in the shortest setup time, intended for new users to get up and running quickly. This is going to be a "headless setup" meaning no peripherals, such as, a screen, keyboard, or mouse are going to be used directly on the Raspberry Pi 0 W. The Raspberry Pi 0 line needs adapters to fit their micro sized ports, which can be a limiting factor for a quick setup. Instead, we'll be controlling everything wirelessly from another computer. Additionally, I've elected to use the full-fledged Raspberry Pi OS instead of the minimal one mainly because it includes Python 3, but also because the desktop interface may be easier for beginners should they choose to use that in the future.

Rpi0W hardware-labelled+cropped

### <ins>PREREQUISITES</ins>

### What you'll need (physically):
- Raspberry Pi 0 W
- microSD card (>= 8GB)
- microSD card adapter
- 5V (2.5A) power supply
- Windows/Mac computer with SD card reader

### What you'll need (digitally):
- Raspberry Pi OS (previously called Raspbian OS), pick one:
  - [ZIP](https://downloads.raspberrypi.org/raspios_full_armhf_latest)
  - [TORRENT](https://downloads.raspberrypi.org/raspios_full_armhf_latest.torrent)
    - NOTE: if you can torrent, that's much faster, the ZIP file seems to be speed limited no matter how fast your internet connection is
- [Balena Etcher](https://www.balena.io/etcher/)

### NOTE:
- If you have any of the Raspberry Pi 0 - 3 models, you'll need Wifi on the 2.4 GHz channel, these models ONLY use this band, and range can be an issue especially on the Raspberry Pi 0 models
- Raspberry Pi 4 can now use either the 2.4 GHz or the 5 Ghz band

### Let's get started:

##### <ins>STEP 1 - Start by downloading all the above links (this could take awhile) and assemble your physical pieces</ins>

- Slot your microSD card into the microSD card adapter
  - This goes into the the SD card slot on your computer (if you don't have one you'll need to get an adapter or dongle)

Rpi0W-setup

##### <ins>STEP 2 - Flash the OS onto the microSD card</ins>

- Open up Balena Etcher

  Rpi0W-Etcher-flash1

  - Flash from file
    
  Rpi0W-Etcher-flash2

  - Select your Raspbian OS ZIP file 

  Rpi0W-Etcher-flash3

  - Select target

  Rpi0W-Etcher-flash4

  - Check your microSD card
    - Size should be anywhere from 8 - 32 GB
      - Raspberry Pi OS needs around 8 GB to install 
      - Sizes > 32 GB will need to be specially reformatted, see [here](https://www.raspberrypi.org/documentation/installation/sdxc_formatting.md)
    - Location should NOT be the main C:\ drive (this is hidden so you don't wipe your entire computer)

  Rpi0W-Etcher-flash5

  - Flash!
    - Windows users: you may need to grant permission to the command line to start the flashing process by selecting "Yes"
 
  Rpi0W-Etcher-flash6

- Windows users: Ignore the Windows warning about a formatting drive error. That will not fix it (instead it will likely wipe your Raspberry Pi OS). However, if Balena Etcher gives you an error, you should be concerned. 

TROUBLESHOOTING FLASHING ERRORS:
If you do have some kind of flash failed error or incomplete
- Go to the Start menu > search for "disk management" > look for your micro SD card partitions (NOT your main computer drive) > right click each one and delete the volumes of your SD card
  - You should be left with a single partition that is the full size of the micro SD card and no other partitions
- Then, use the [official SD card formmater](https://www.sdcard.org/downloads/formatter/) program to wipe your SD card
- Start the procedure over from the Balena Etcher flashing steps
- Alternatively, you can attempt to use the [official Raspberry Pi Imager](https://www.raspberrypi.org/downloads/) which is based off the Pi Bakery tool.
(TO DO: take pictures of this)

##### <ins>STEP 3 - Prepare the boot partition</ins>

  If you scroll to the top of this page, you will see the [boot_files](https://github.com/eugf/raspberry_pi_setup_guide/tree/master/boot_files) folder. You can either download this entire GitHub repository and extract those two boot files, or copy and paste the contents into your own text files on your computer.

If you're copy pasting onto your own computer:

Windows users:
- Open up My Computer > select the microSD card (for me it's the F:\ drive) > right click somewhere away from the file names > New > Text document 
  - Right click the file > Rename > Change the name and the extension to 
    ```
    ssh
    ```
    with NO EXTENSION (be sure to delete the .txt at the end)
- Repeat these steps to make a second file, but this time copy and paste the text inside the wpa_supplicant.conf file into your blank text file
  - Change the network SSID (your wifi name) and the network PSK (your wifi password) to match your own home network
  - Save and close the file
  - Right click the file > Rename > Change the name and extension to 
    ```
    wpa_supplicant.conf 
    ```
    (be sure to delete the .txt at the end)
  
Rpi0W-boot

Mac users:
- Open up TextEdit > Go to the Format option > change it to "Plain Text" 
  - Save the file
    - Select Unicode-8
    - Uncheck the .txt option
  - Make sure the full name is  
    ```
    ssh
    ```
    without any other extension (you might need to right click and view info or detailed properties and uncheck "hide extension" to see this)
    
- Open up TextEdit > Go to the Format option > change it to "Plain Text" > copy and paste the text inside the wpa_supplicant.conf file into your blank text file
  - Change the network SSID (your wifi name) and the network PSK (your wifi password) to match your own home network
  - Save the file
    - Select Unicode-8
    - Uncheck the .txt option
  - Make sure the full name is  
    ```
    wpa_supplicant.conf 
    ```
    without any other extension (you might need to right click and view info or detailed properties and uncheck "hide extension" to see this)

If you're using a hidden network, an unsecured network, an extremely long  password or want some special configurations, see [here](https://www.raspberrypi.org/documentation/configuration/wireless/wireless-cli.md) for more details on how to set that up

Once you have your 2 files (ssh and wpa_supplicant.conf) move them into your microSD card
  - These files will disappear once you boot up the Raspberry Pi
  - If you need to edit them again, you'll need to reverse the procedure and add the ".txt" extension at the end of the file name to view and edit them in a regular text editor

- Eject
  - Windows users: Right click the USB/attached drive icon in the bottom right of the task bar
    - Select your microSD card
      - It should say "[your microSD card drive letter] can be safely removed now"
  - Mac users: Drag the icon for the microSD card drive to the eject icon
  - If it's a spring-loaded type, you can press the card deeper into the slot and it should pop back out. If you have the kind where the SD card sticks out then it won't have a spring and can be easily removed with your fingers

Rpi0W-Etcher-flash7

##### <ins>STEP 4 - Raspberry Pi</ins>

You're finally ready to setup the physical Raspberry Pi!
- Take the microSD card out of the microSD card adapter, and slot it into the Raspberry Pi
- Connect the power plug to the slot that is labelled "PWR IN"
- You should see a green light in the corner (close to the "PWR IN" plug) if the power is on and the OS boots correctly

Rpi0W-ON

##### </ins>STEP 5 - SSH</ins>

### Ping test

Windows users:
- Go to the Start menu > type in "cmd" > run the Command Prompt program

Mac users:
- Go to your applications and search for the Terminal program

From here both users can do a quick test to see if their Raspberry Pi is properly connected to the network
- Type in:
  ```
  ping raspberrypi.local 
  ```

Rpi0W-ping-B W

- Make note of the IP address this returns, which in my case starts with "192.###.##.###", yours should be formatted similarly as four sections with up to three-digit numbers separated by three periods.
- Alternatively, if your IP address returns letters and numbers such as "2001:#xx#:##x#:####:####:#x#x:####:####" with eight sections with four characters in each, separated by periods between the sections, you have an IPv6 address. This is expected to become more commonplace and will work fine.
- If you have no response and it's been at least several minutes since the Raspberry Pi was booted up, try moving it closer to the router and try to ping again

Mac users:
- Cancel the ping by pressing control + C

### Now we can actually try to SSH

Easy way:

Use this if you've only got one Raspberry Pi on the whole network
- From the Terminal > type in:
  ```
  ssh pi@raspberrypi.local
  ```

More tech savvy way:

Use this if you're managing multiple Raspberry Pi's on the same network, you'll need this to specify which one. Or if you're changing OS's often or connecting to many Pi's
- From the Terminal > type in:
  ```
  ssh pi@192.xxx.xx.xxx
  ```
  - Replace the digits after the @ symbol with your Raspberry Pi's IP address
  - If you have an IPv6 address you can select the IP address from the ping results, copy and paste it here (right clicking will aid with that)
  - See [here](https://www.servermania.com/kb/articles/ssh-mac/) for more info for Mac users

For a more advanced method, good especially if you're handling multiple Raspberry Pi's or want a one click solution or are getting errors, see my [PuTTY section](https://github.com/eugf/raspberry_pi_setup_guide/blob/master/PuTTY.md) 

Rpi0W-SSH warning

You may have to type in "yes" and hit enter to proceed

##### <ins>STEP 6 - Logging into the Pi</ins>

  Once you've successfully connected over SSH, you are now operating over the command line in the Raspberry Pi, also called "command line interface" (CLI). At this point, your computer is remotely accessing your Raspberry Pi and can run any programs on it (provided you know what to type in). But first, it will ask for the default login credentials of the Raspberry Pi, which we are going to change IMMEDIATELY for security reasons.

- Login as
  ```
  pi
  ```
- Password is 
  ```
  raspberry
  ```

This is the command for changing the password 

- Type in:
  ```
  passwd
  ```
- Enter the default password
  ```
  raspberry
  ```
- Now enter your desired password twice

  Rpi0W-passwd
  
Congrats! You are now ready to start using your Raspberry Pi! 

##### <ins>STEP 7 - Handy extras</ins>

For a simple GUI based way to edit important system settings, such as:
- passwords
- wifi networks
- SSH, VNC
- overclocking
- Remote GPIO, SPI, I2C, serial, camera connections

You can use the command:
``` 
sudo raspi-config 
```

sudo raspi-config

***One more thing: always shut down properly by typing in***
```
sudo halt
```
***The green light in the corner will blink a few times before turning off. Now you can unplug the power. Unplugging it before a proper shutdown (either from command line or from the desktop interface's shutdown button) can result in [data corruption on the microSD card](https://www.raspberrypi.org/forums/viewtopic.php?t=36533#:~:text=If%20you%20loose%20power%20when,when%20the%20Pi%20is%20running.) which can eventually destroy the micro SD card and whatever data you had on it. If your setup did not work for some reason and you have the adapters for HDMI and the microUSB to regular USB for a keyboard, plugging those in would be the easiest way to check this. If not, you can unplug it and start over but try to keep this to a minimum***

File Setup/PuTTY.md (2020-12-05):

### Who is this for?
If you start to manage many Raspberry Pi's it might be work getting an SSH client, such as PuTTY

Running the ssh pi@raspberrypi.local command to connect to multiple Raspberry Pi's can cause errors if you:
- have multiple Raspberry Pi's
- change OS's frequently (by flashing the card and connecting again)
- change the Wifi network
- OR, are under an active network intrusion (please be sure to change your password IMMEDIATELY upon setting up your Raspberry Pi the first time, this the minimum you can do to protect yourself)

Example
Rpi0W-SSH warning-DNS spoofing

Windows users: [PuTTY](https://www.chiark.greenend.org.uk/~sgtatham/putty/latest.html)
- Choose 64-bit if your OS can support it, if you're not sure what you have, it's fine to use 32-bit then
- Under Package Files > MSI: Choose the 64-bit files if your OS can support it, if you're not sure what you have, it's fine to use 32-bit then

Open up the PuTTY program > type in the IP address (or try all of them if you have multiple results returned from ping) > open
  - It will give you a warning, select "Yes"

PuTTY

Saving your IP address for future use:
1. You need to be in the "Session" category (default) on the left
2. Enter the IP address of your Raspberry Pi here
3. Name your session
     - I would suggest something descriptive such as "Rpi0W-OpenPlant-192.xxx.xx.xxx", this way you know what project it is and what IP address it was in case you need to check against a list of multiple IP addresses if you have many Raspberry Pi's
      - In any case this makes future access as simple as opening PuTTY and double clicking the "name" you've given it, so make sure you can recognize it
4. Click Save
      - It will now populate the empty white box left of the save button with your named session
     - From now on you can just double click that name to reconnect

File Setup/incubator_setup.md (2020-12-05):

This part is specifically for Genspace NYC's OpenPlant group, and it assumes you have the hardware all setup and connected (Rpi0 + PCB + camera + LED's).
This will then install the software needed to operate aforementioned components. 

SSH onto your Rpi0 and run this command:

```
pip3 install git+https://github.com/genspace/openplant-incubator
```

Then run 
```
incubate-me
```

If this is your first time installing a python package onto your pi, you may need to run the following command if the Raspberry Pi is unable to locate the `incubate-me` command:

```
source ~/.profile
```

The `incubate-me` command will prompt you for a password to decrypt secrets needed to connect to the AWS server. You will need to get a password from the Genspace NYC's OpenPlant group and enter the value when prompted.

```
*** C L A S S I F I E D ***
```

The script will also prompt the user to enter in a set of configuration values at first start-up. You can just accept the defaults by hitting return on your keyboard, except for the `INCUBATOR_NAME` parameter. You must assign you own name for this value. No spaces should be used in this value. 

If you would like to edit the values in your configuration file at some future date, simply enter `set-config` to reconfigure the system configuration settings.

To upgrade the script to the latest version, run this command:

```
pip3 install --upgrade git+https://github.com/genspace/openplant-incubator.git
```

Optional:
- If you'd like to see the data graphically, you're going to need the URL and password from Genspace's OpenPlant group to access the Metabase 
```
*** C L A S S I F I E D ***
```

Please request access for for those resources

Tmux Setup:
- Install tmux with 
  ```
  sudo apt install tmux
  ```
- Type ```tmux``` and then hit Enter
- This will start a Tmux session to detach the session and let it continue running even if you are no longer on SSH

Tmux Useful Shortcuts & Commands:

Control + B, then press C = create new window (virtual session with 0, 1, 2, etc)

Control + B, then press # = go to that window

Control + B, then press D = detach and run in background

```tmux attach``` = bring to foreground

```exit``` = closes one of the windows, whichever one you're active in

If you try to enter tmux again through the plain tmux command it will wipe existing session and start a new one
Once you've detached the tmux you can run it in the background and allow your incubate-me command to run in the background

TODO:

Need to get it on cron/systemd/tmux to run as a background process
Need to get extra motors

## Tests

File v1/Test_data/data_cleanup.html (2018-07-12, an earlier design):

# Analyzing the performance of the OpenPlant incubator at Genspace

- Read in data and preprocess
- Visualze the data

sessionInfo() #for reproducibility

## R version 3.5.0 (2018-04-23)
## Platform: x86_64-redhat-linux-gnu (64-bit)
## Running under: Fedora 27 (Twenty Seven)
## 
## Matrix products: default
## BLAS/LAPACK: /usr/lib64/R/lib/libRblas.so
## 
## locale:
##  [1] LC_CTYPE=en_CA.UTF-8       LC_NUMERIC=C              
##  [3] LC_TIME=en_CA.UTF-8        LC_COLLATE=en_CA.UTF-8    
##  [5] LC_MONETARY=en_CA.UTF-8    LC_MESSAGES=en_CA.UTF-8   
##  [7] LC_PAPER=en_CA.UTF-8       LC_NAME=C                 
##  [9] LC_ADDRESS=C               LC_TELEPHONE=C            
## [11] LC_MEASUREMENT=en_CA.UTF-8 LC_IDENTIFICATION=C       
## 
## attached base packages:
## [1] stats     graphics  grDevices utils     datasets  methods   base     
## 
## other attached packages:
## [1] ggplot2_3.0.0  stringr_1.3.1  tidyr_0.8.1    dplyr_0.7.6   
## [5] readr_1.1.1    rmarkdown_1.10 knitr_1.20    
## 
## loaded via a namespace (and not attached):
##  [1] Rcpp_0.12.17     bindr_0.1.1      magrittr_1.5     hms_0.4.2       
##  [5] munsell_0.5.0    tidyselect_0.2.4 colorspace_1.3-2 R6_2.2.2        
##  [9] rlang_0.2.1      plyr_1.8.4       tools_3.5.0      grid_3.5.0      
## [13] gtable_0.2.0     withr_2.1.2      htmltools_0.3.6  lazyeval_0.2.1  
## [17] yaml_2.1.19      rprojroot_1.3-2  digest_0.6.15    assertthat_0.2.0
## [21] tibble_1.4.2     bindrcpp_0.2.2   purrr_0.2.5      glue_1.2.0      
## [25] evaluate_0.10.1  stringi_1.2.3    compiler_3.5.0   pillar_1.2.3    
## [29] scales_0.5.0     backports_1.1.2  pkgconfig_2.0.1

# Read in data and preprocess

Declare the labels for the columns and list the files which will be read into the data table. Then prep the master data table as tidy data.

labels <- c("time", "temp", "humidity", "lux", "input", "fan", "output")
files <- c("180703.LOG", "180704.LOG", "180705.LOG", "180706.LOG","180707.LOG", "180708.LOG", "180709.LOG", "180710.LOG")

working_data <- lapply(files, read_csv, col_names = labels) %>%
  bind_rows() %>%
  transform(time = as.POSIXct(strptime(time, "%Y%m%d_%H:%M:%S"))) %>%
  select(-input, -fan) %>%
  gather(measure, value, -time) %>%
  arrange(time, measure)

# Visualze the data

plot the measures

ggplot(data = working_data, aes(x = time, y = value)) +
  #scale_color_brewer(palette = "Set1") +
  geom_line() +
  #geom_line(aes(alpha = 0.5)) +
  #geom_line(aes(x = rollmean(time, 3, fill = NA), y = rollmean(value, 3, fill = NA), colour = measure)) +
  facet_grid(measure ~ ., scales = "free_y")

ggplot(data = filter(working_data, format(time, "%m%d") == "0707"), aes(x = time, y = value)) +
  geom_line() +
  facet_grid(measure ~ ., scales = "free_y")

zoom into the interesting features on July 7

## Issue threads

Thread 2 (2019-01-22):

### ISSUE TITLE
BME280???

### ISSUE THREAD

**Issue by MFernflower** [genspace/openplant-incubator#2]
https://www.adafruit.com/product/2652

Despite the fact that it's 20 dollars for the sensor it might be worth updating the code to use a single bme280 in the center of the incubator box to check the environment  - it can also sense barometric pressure if one is interested 

I think it's worth the upfront price as only one i2c sensor is needed to monitor the whole incubator environment!

**Comment by danwchan** [comment]
The current code assume the use of the SHT31 sensor which can measure the temperature and humidity. There is no direct control over humidity and likely the plants experience a different humidity in their sealed petri dishes so I view the humidity data as extraneous (even though I collect it). I think the sensing of pressure is similarly extraneous.

I recently updated the code however which would make adapting the incubator to other hardware options easier. I won't be incorporating the BME280 sensor into the build without better rationale, but if you want to use that component now would be a good time to fork the project and edit the code.

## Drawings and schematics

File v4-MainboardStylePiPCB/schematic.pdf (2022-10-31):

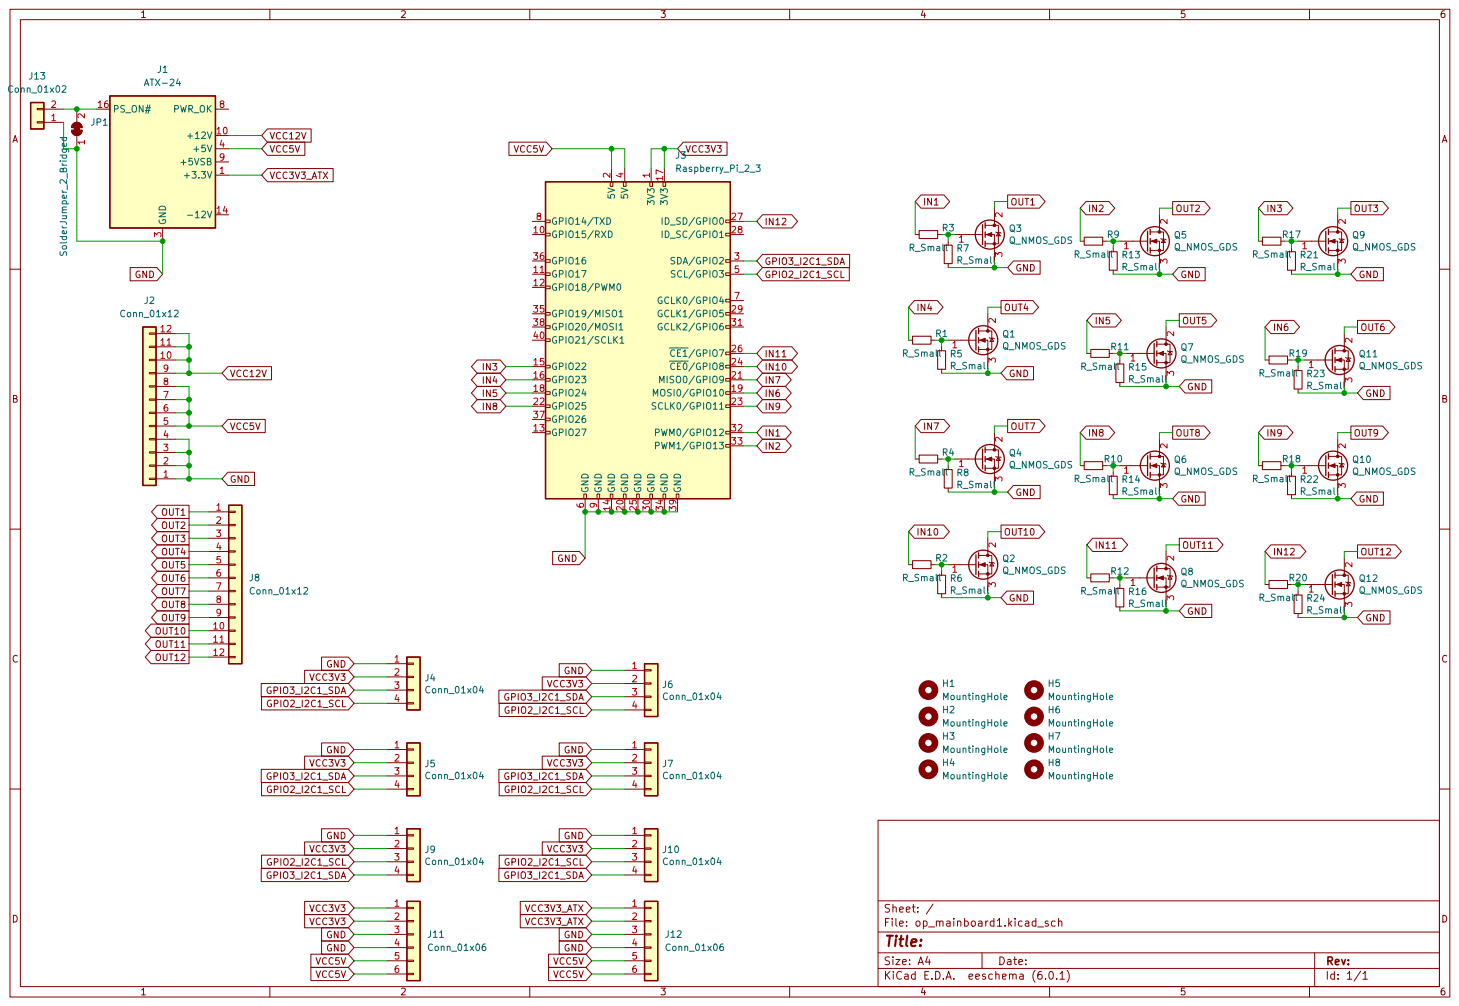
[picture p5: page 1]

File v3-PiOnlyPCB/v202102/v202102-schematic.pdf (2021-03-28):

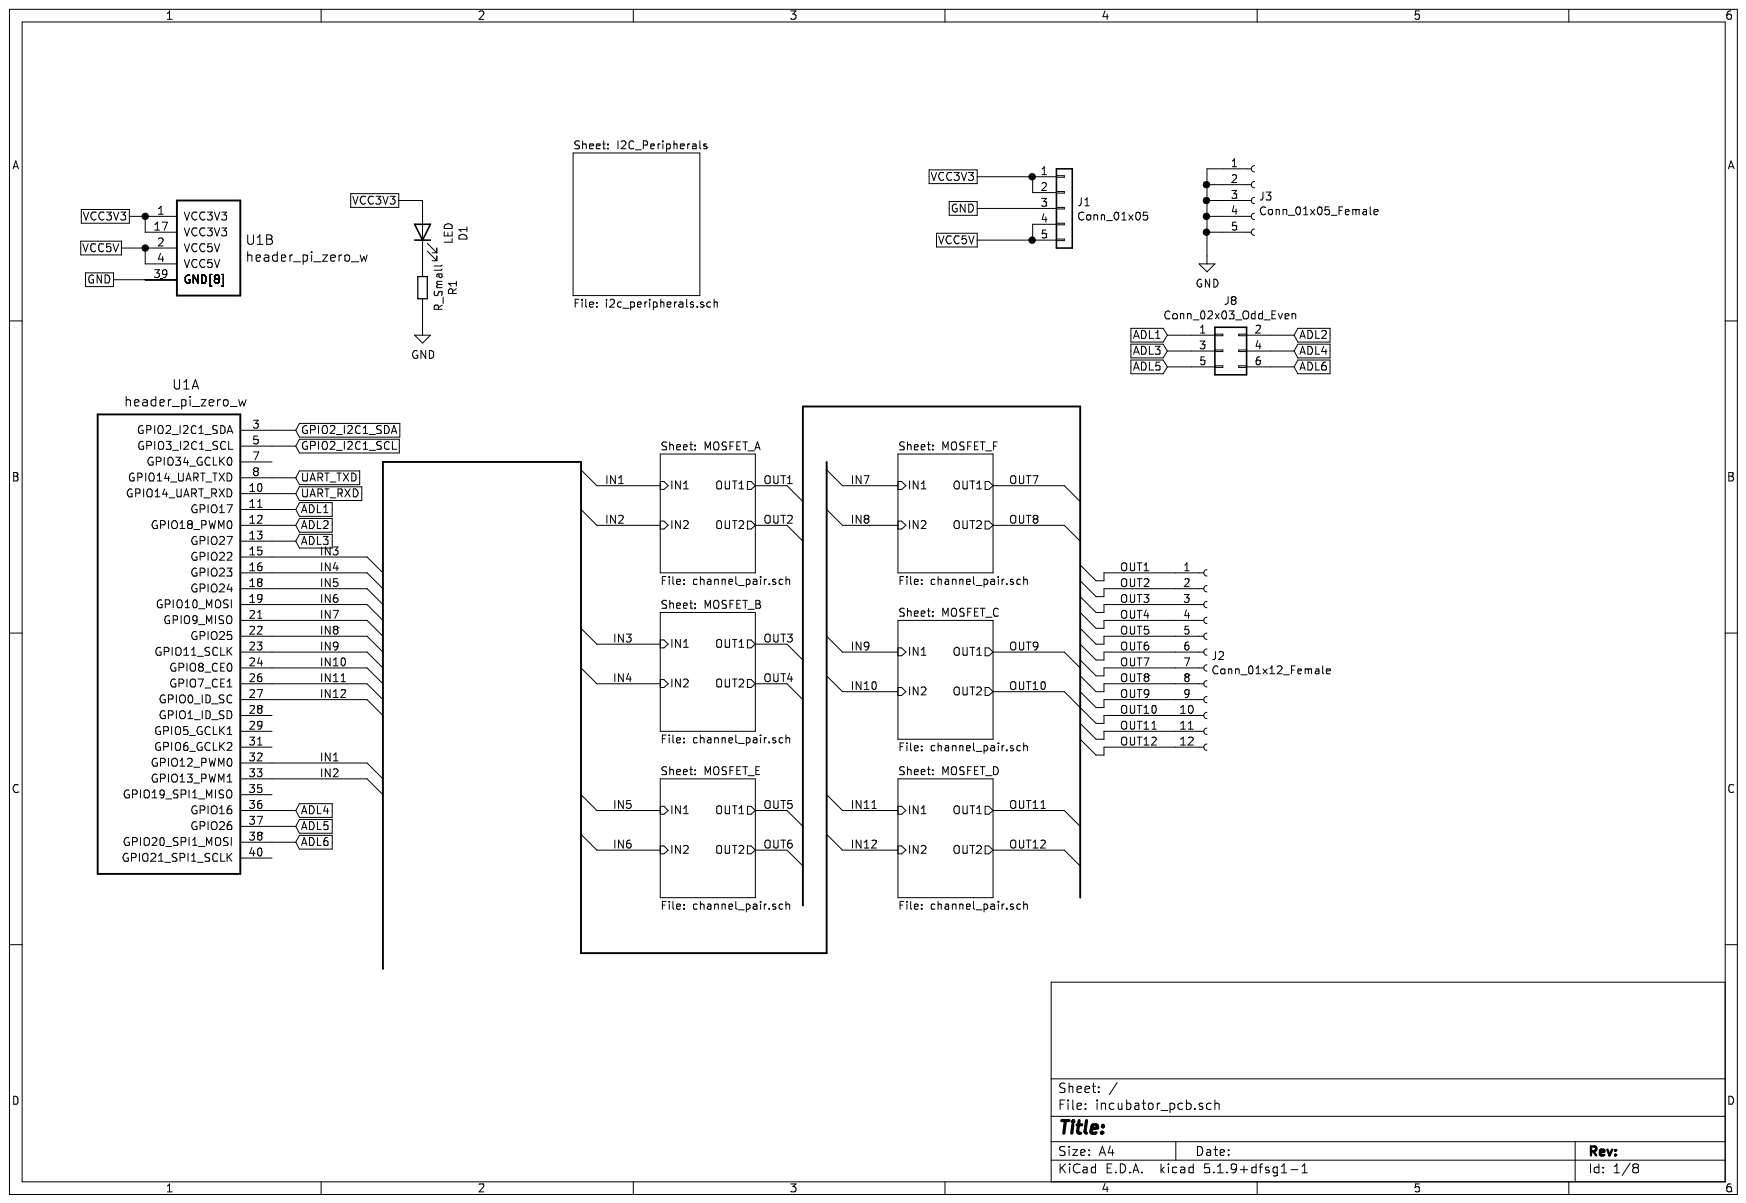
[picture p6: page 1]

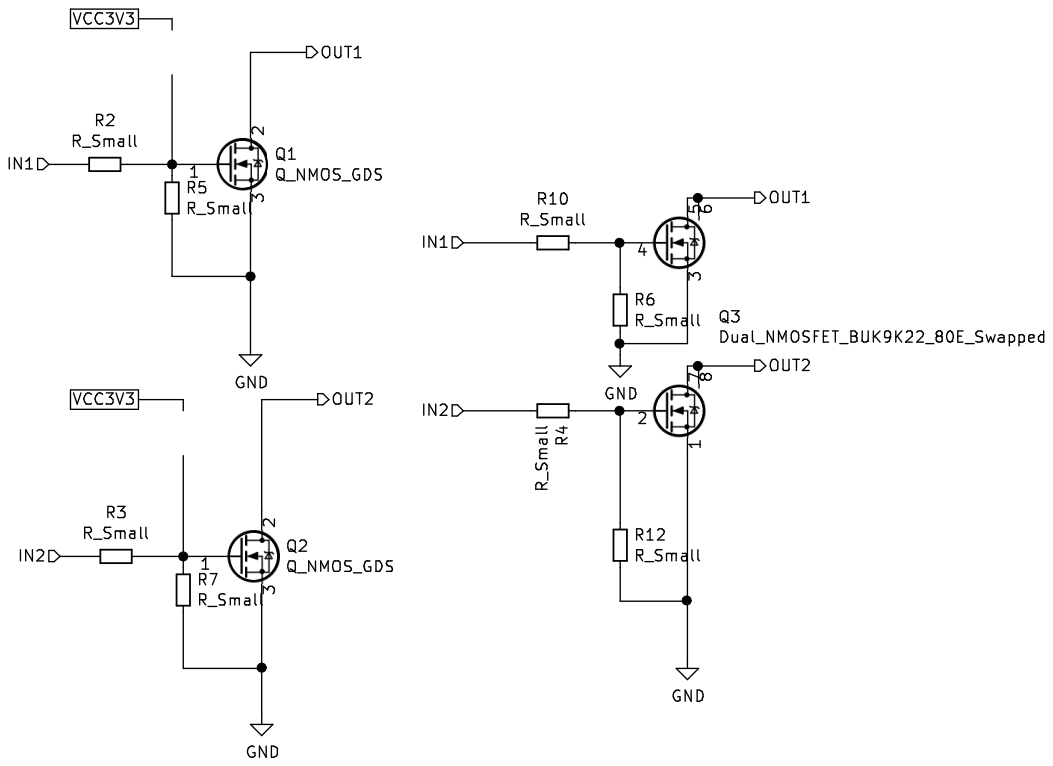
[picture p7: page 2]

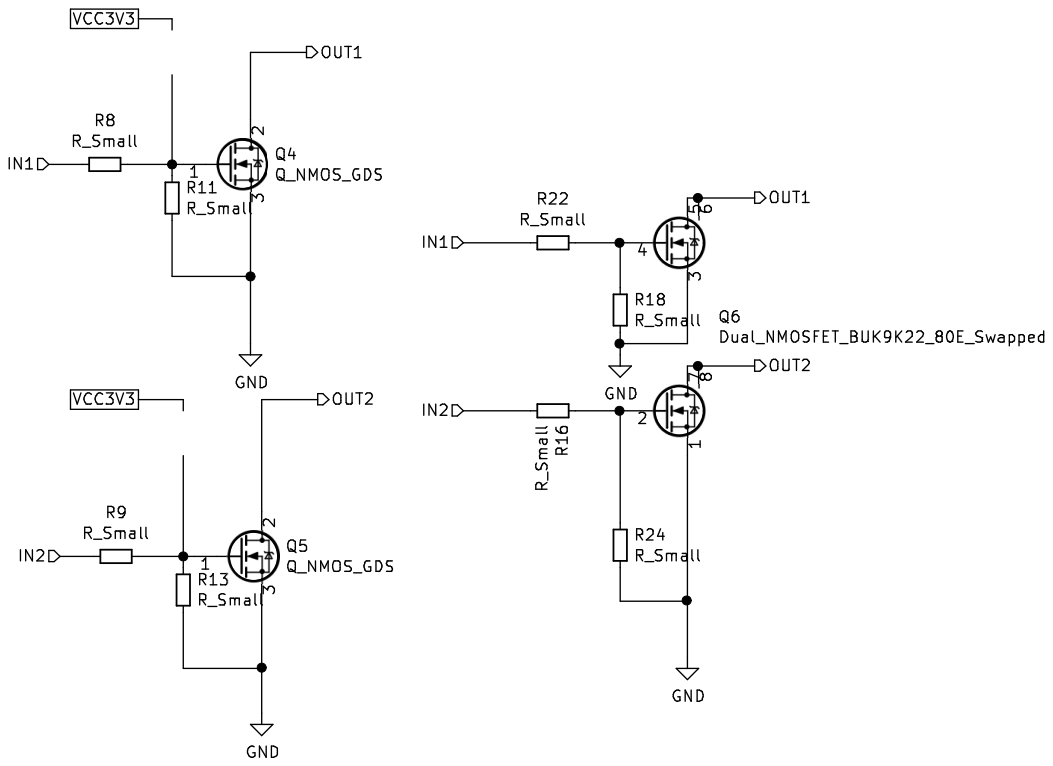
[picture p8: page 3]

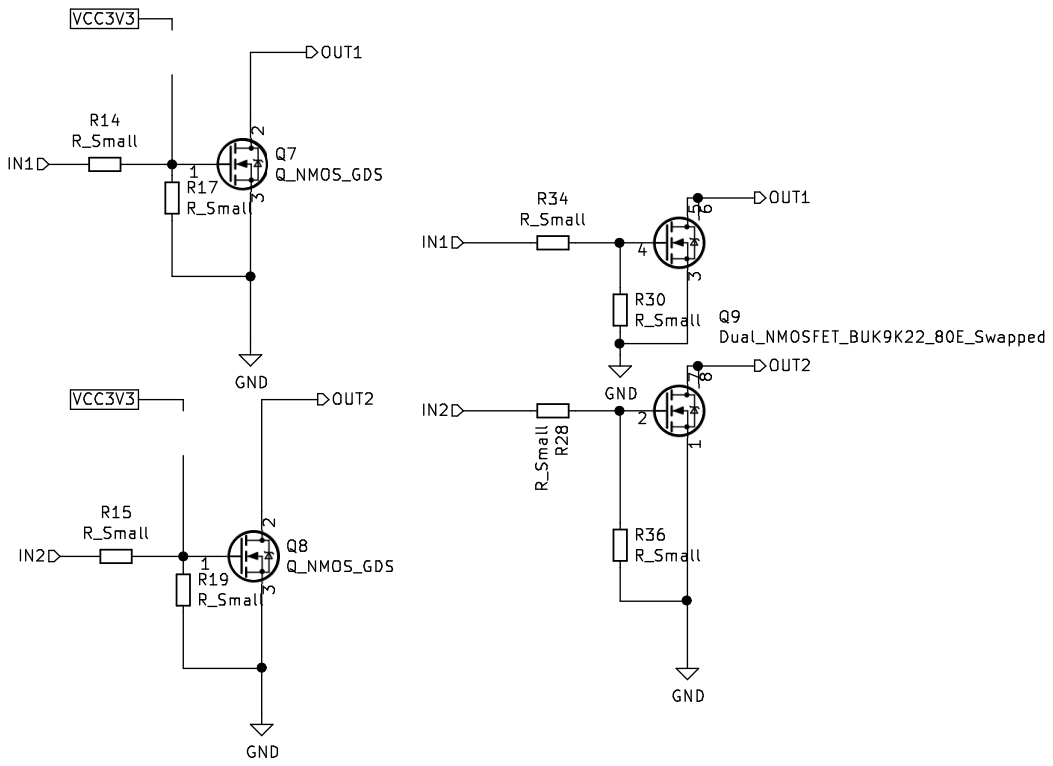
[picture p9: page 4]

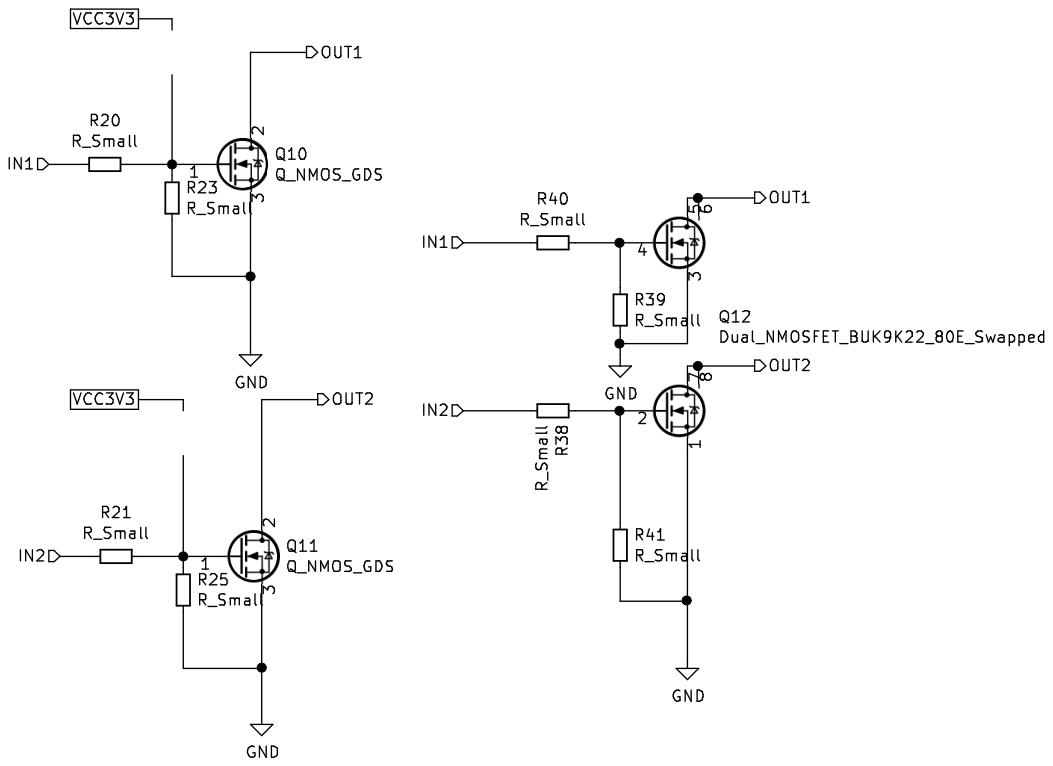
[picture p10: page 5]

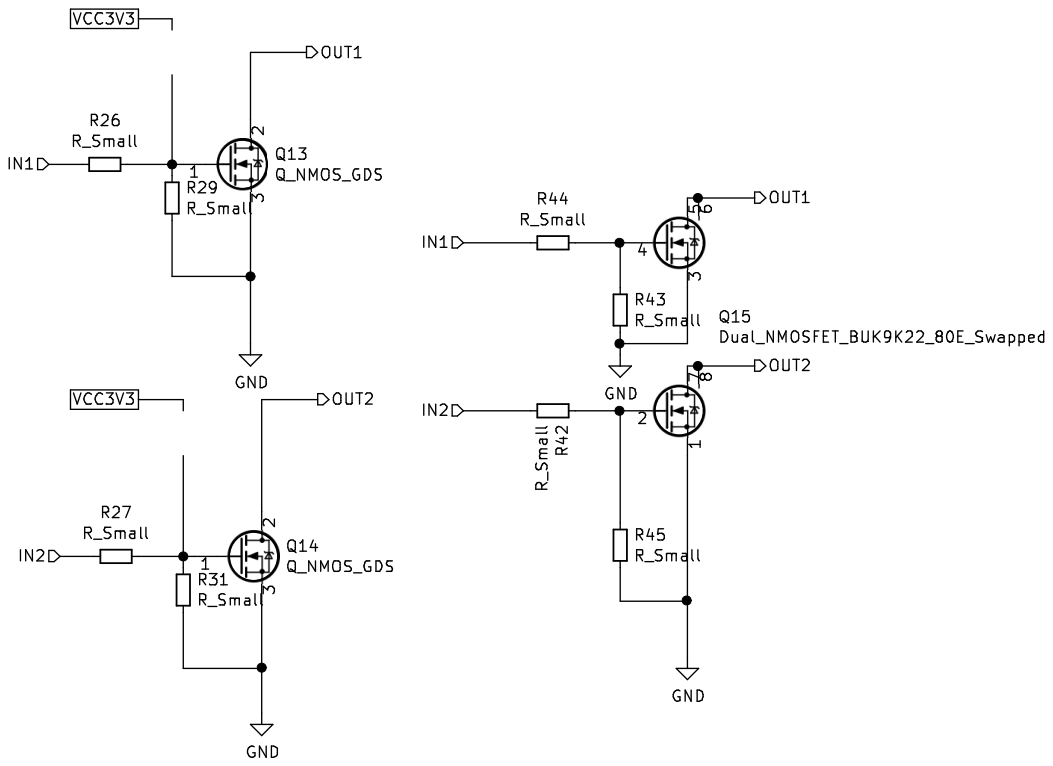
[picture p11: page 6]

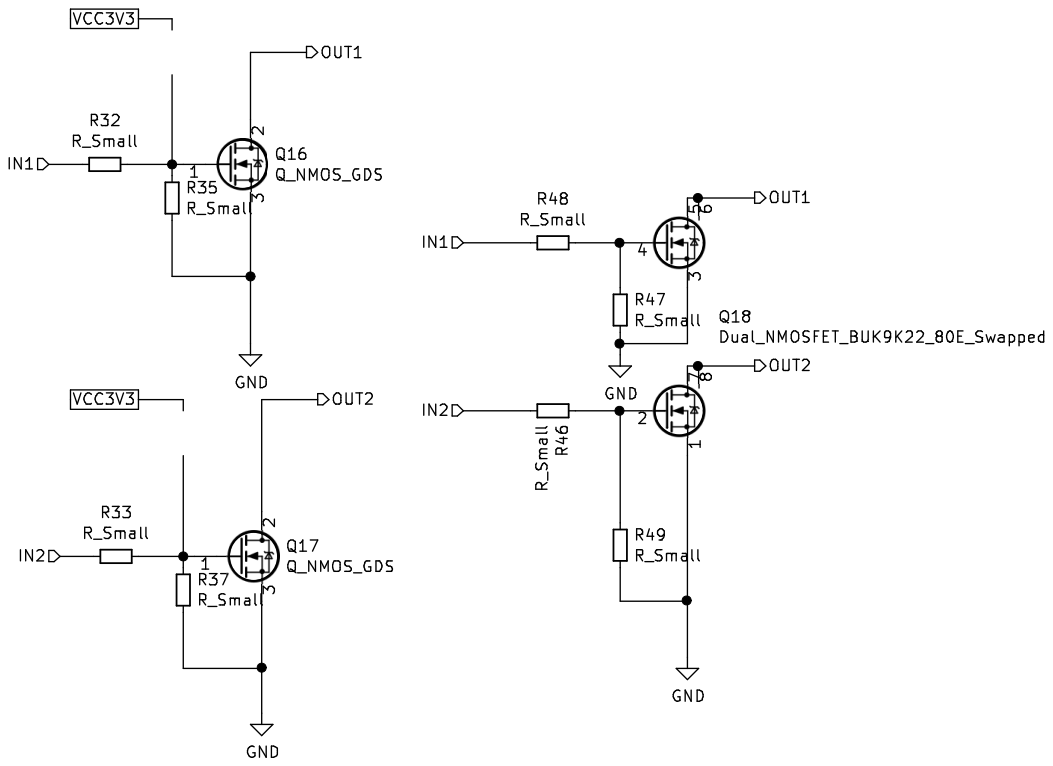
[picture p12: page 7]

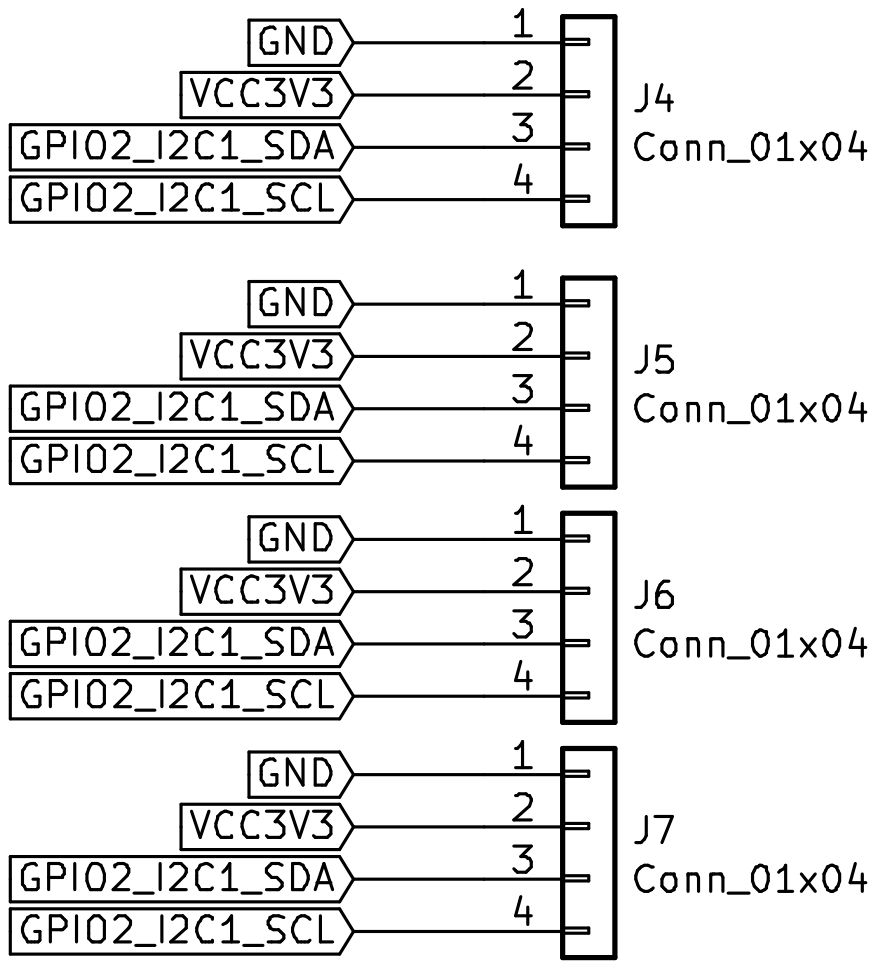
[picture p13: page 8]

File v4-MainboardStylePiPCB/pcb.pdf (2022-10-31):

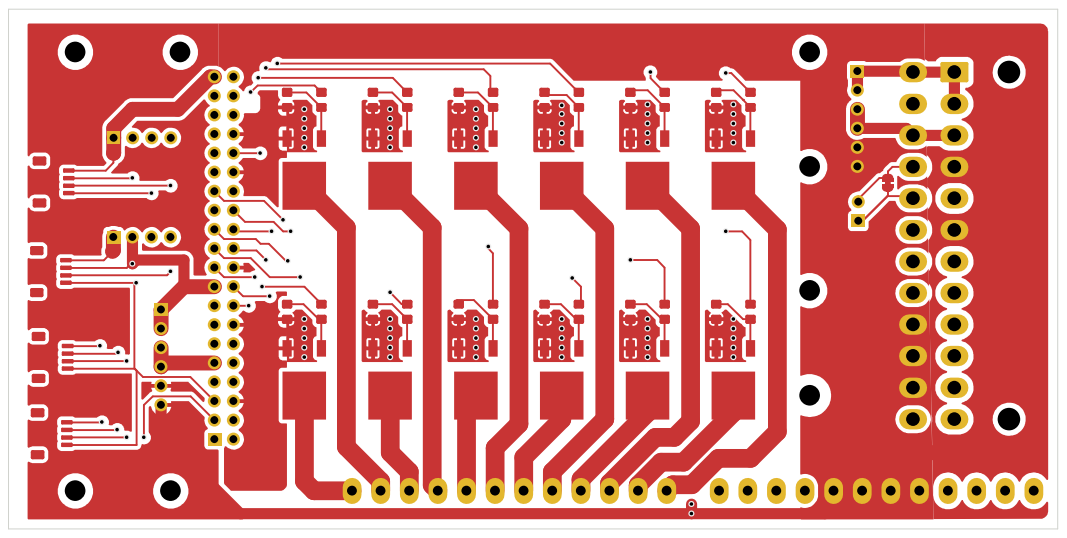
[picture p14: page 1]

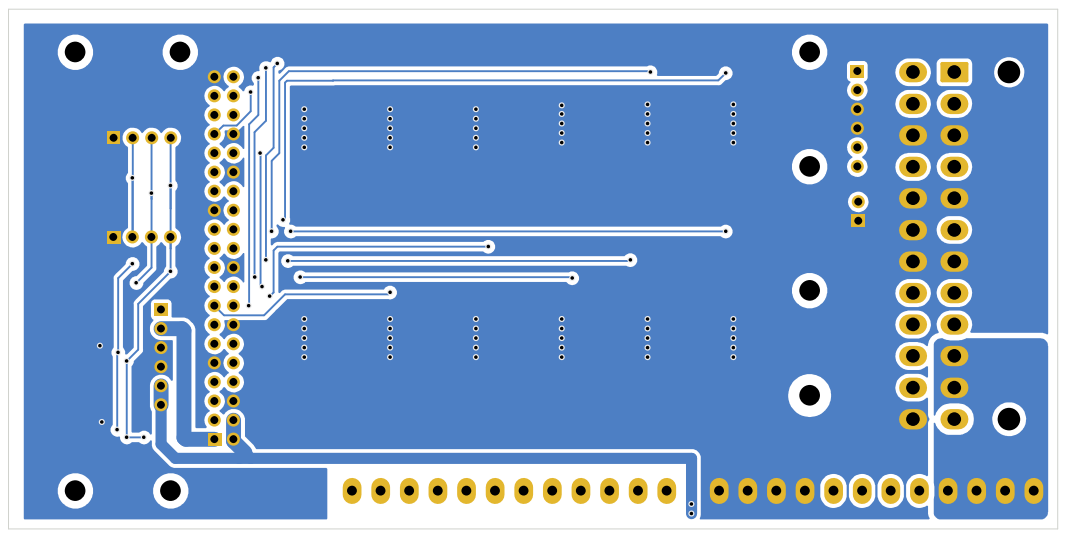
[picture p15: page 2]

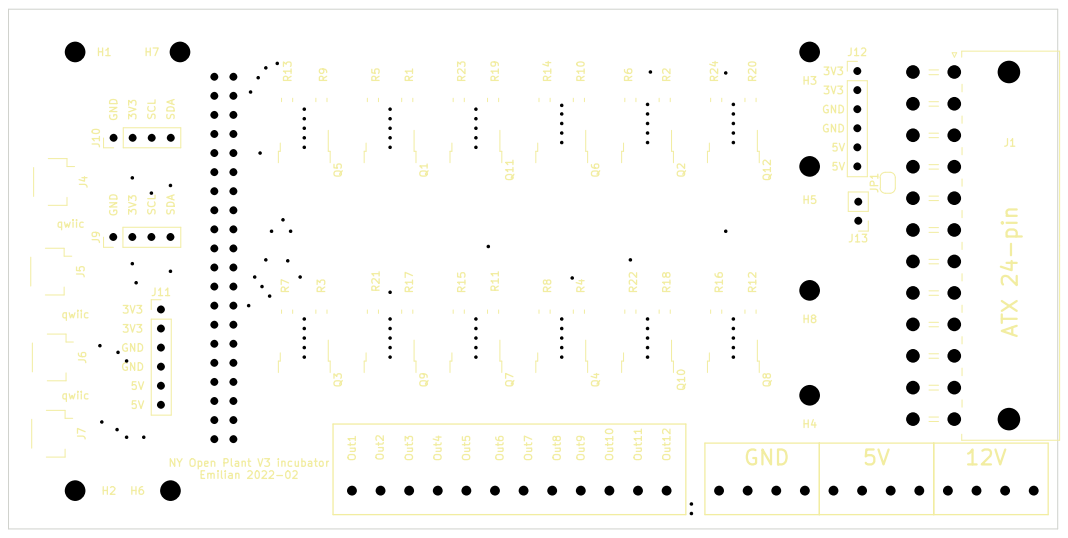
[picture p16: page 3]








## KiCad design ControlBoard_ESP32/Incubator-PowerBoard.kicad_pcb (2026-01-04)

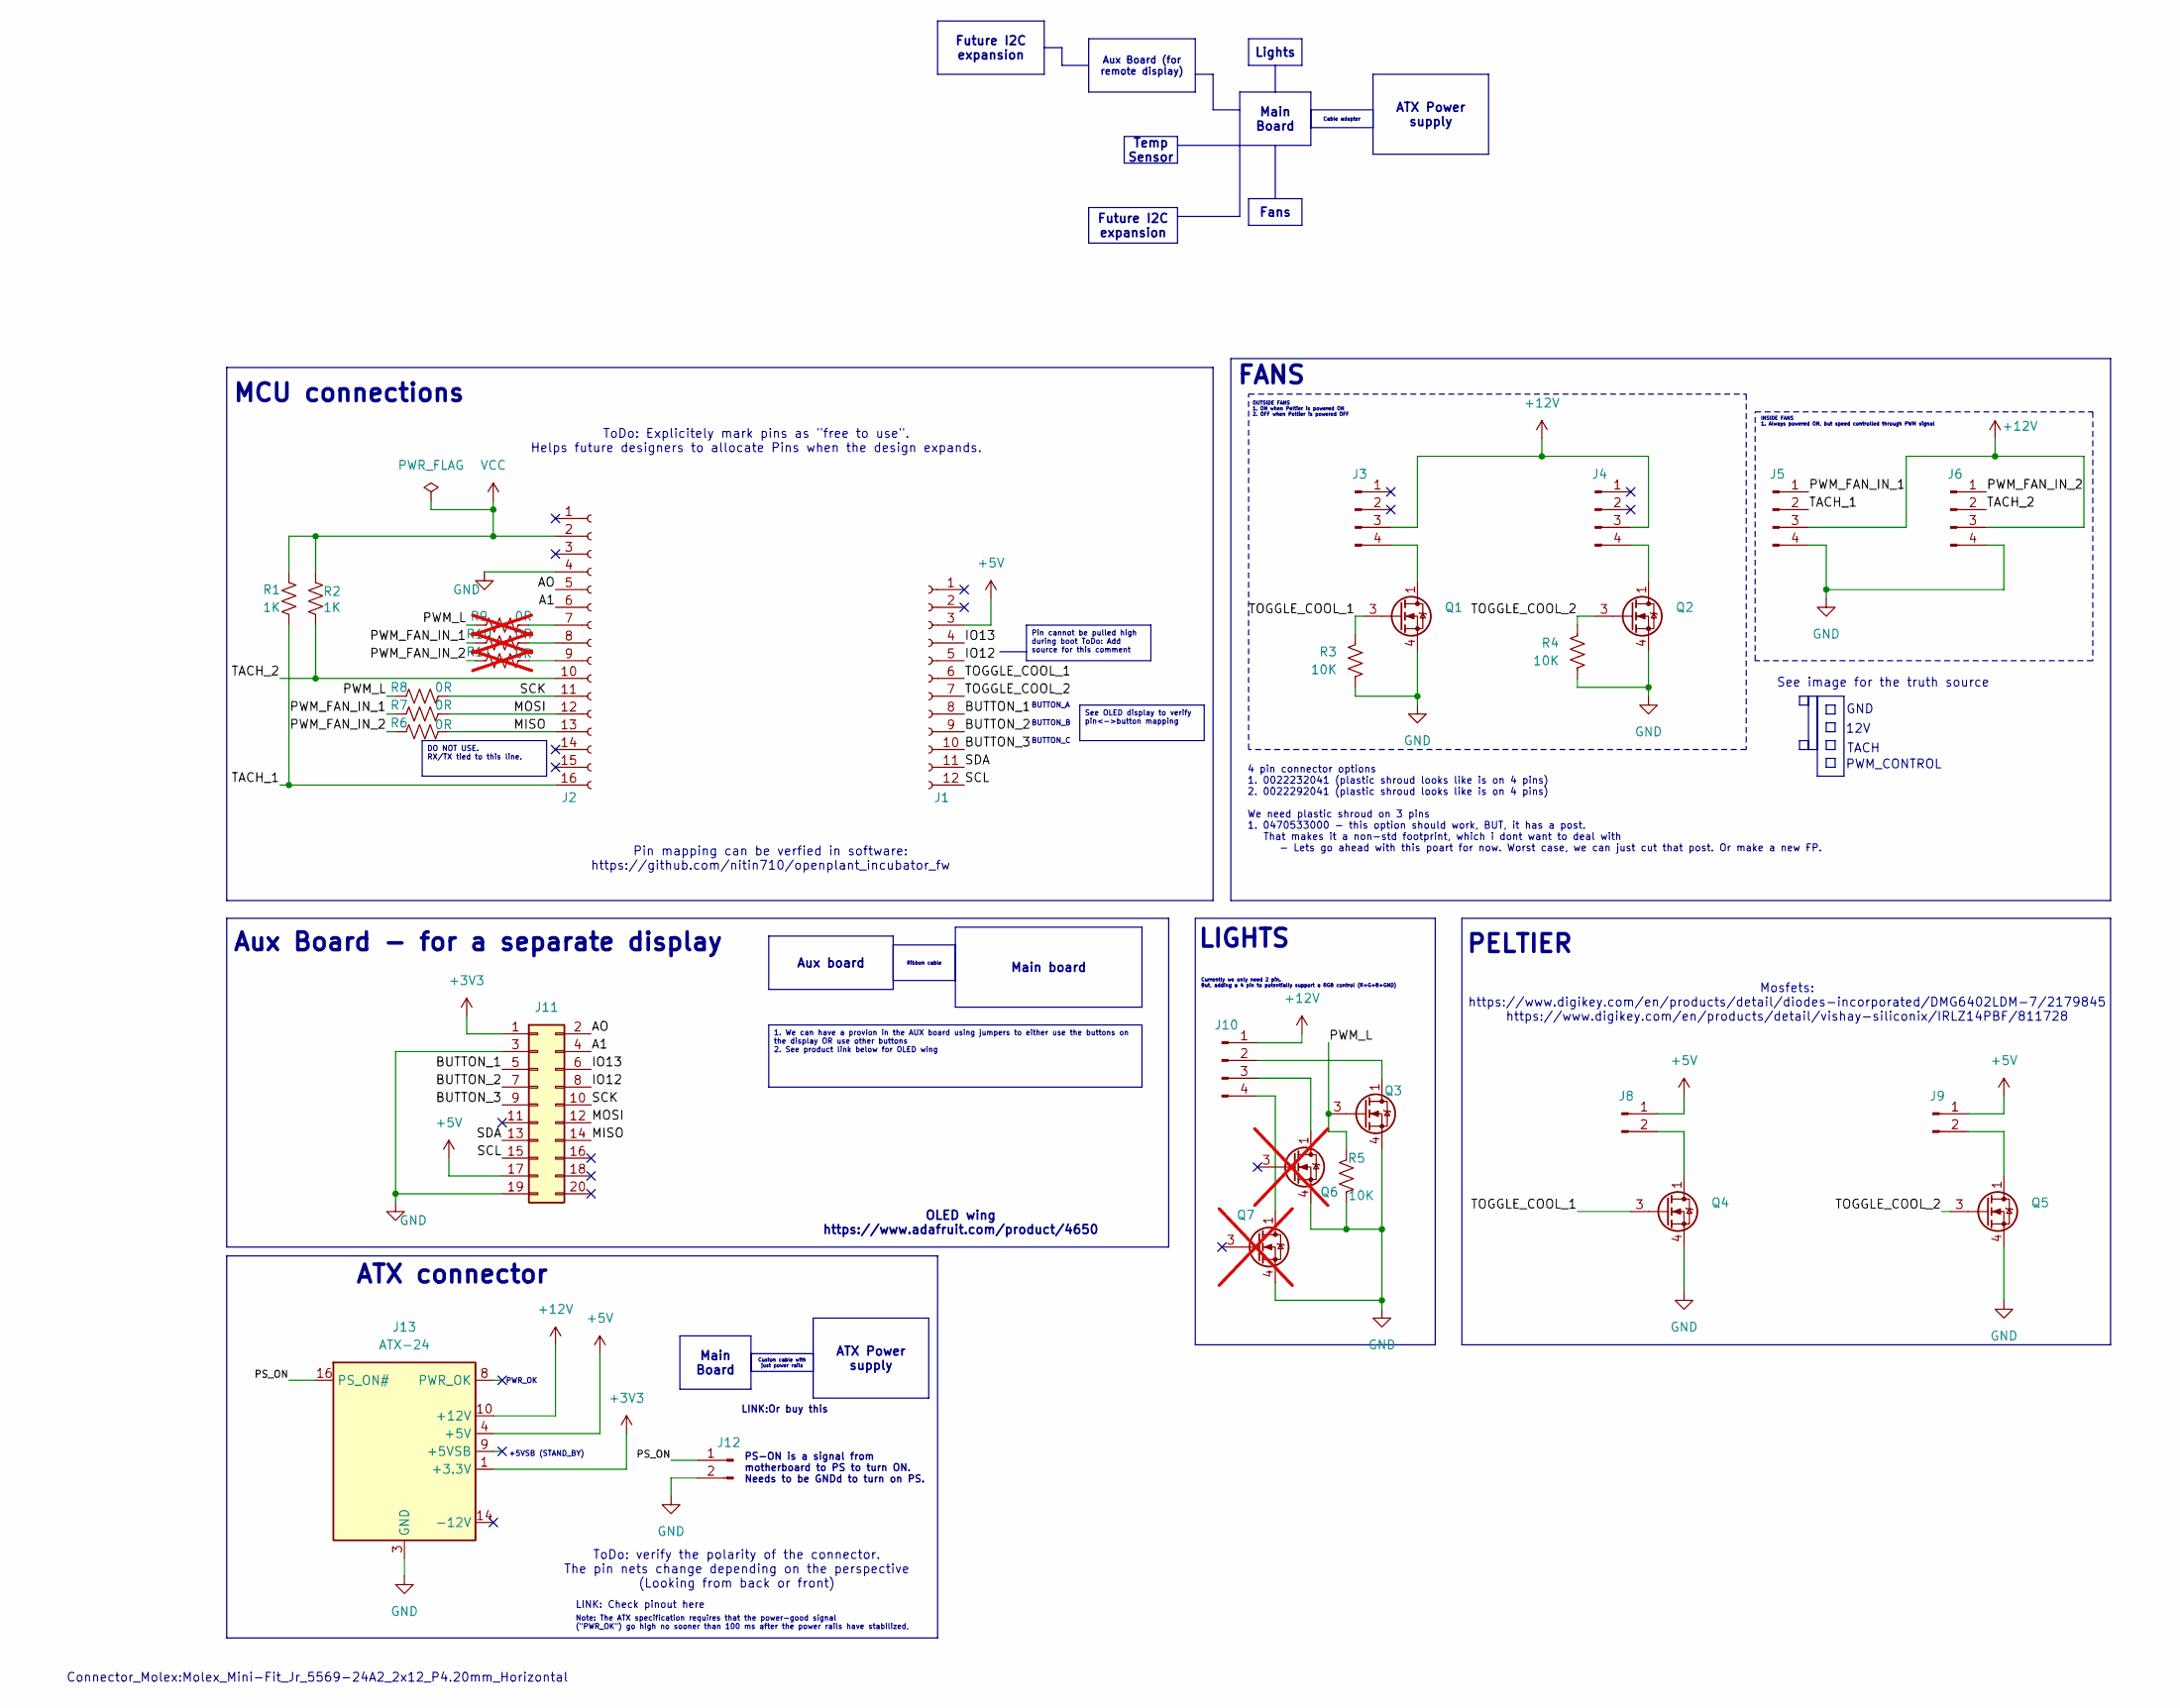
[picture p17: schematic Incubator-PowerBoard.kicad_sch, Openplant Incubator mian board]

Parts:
J1: Conn_01x12_Socket; PinSocket_1x12_P2.54mm_Vertical; MPN PPTC121LFBN-RC; Digikey_Part_Number S6100-ND
J2: Conn_01x16_Socket; PinSocket_1x16_P2.54mm_Vertical; MPN PPTC161LFBN-RC; Digikey_Part_Number S7014-ND
J3: OUT_FAN_1; PinHeader_1x04_P2.54mm_Vertical; MPN 61300411121; Digikey_Part_Number 732-5317-ND
J4: OUT_FAN_2; PinHeader_1x04_P2.54mm_Vertical; MPN 61300411121; Digikey_Part_Number 732-5317-ND
J5: IN_FAN_1; PinHeader_1x04_P2.54mm_Vertical; MPN 61300411121; Digikey_Part_Number 732-5317-ND
J6: IN_FAN_2; PinHeader_1x04_P2.54mm_Vertical; MPN 61300411121; Digikey_Part_Number 732-5317-ND
J8: PELTIER_1; PinHeader_1x02_P2.54mm_Vertical; MPN 61300211121; Digikey_Part_Number 732-5315-ND
J9: PELTIER_2; PinHeader_1x02_P2.54mm_Vertical; MPN 61300211121; Digikey_Part_Number 732-5315-ND
J10: LIGHTS; PinHeader_1x04_P2.54mm_Vertical; MPN 61300411121; Digikey_Part_Number 732-5317-ND
J11: Conn_02x10_Odd_Even; PinHeader_2x10_P2.54mm_Vertical
J12: Conn_01x02_Pin; PinHeader_1x02_P2.54mm_Vertical; MPN 61300211121; Digikey_Part_Number 732-5315-ND
J13: ATX-24; Molex_Mini-Fit_Jr_5569-24A2_2x12_P4.20mm_Horizontal
Q1: OUT_FAN_1; SOT-23-6; MPN DMG6402LVT-7; Digikey_Part_Number DMG6402LVT-7DICT-ND
Q2: OUT_FAN_2; SOT-23-6; MPN DMG6402LVT-7; Digikey_Part_Number DMG6402LVT-7DICT-ND
Q3: LIGHTS; SOT-23-6; MPN DMG6402LVT-7; Digikey_Part_Number DMG6402LVT-7DICT-ND
Q4: PELTIER_1; SOT-23-6; MPN DMG6402LVT-7; Digikey_Part_Number DMG6402LVT-7DICT-ND
Q5: PELTIER_2; SOT-23-6; MPN DMG6402LVT-7; Digikey_Part_Number DMG6402LVT-7DICT-ND
Q6, Q7: DMG6402LVT-7; SOT-23-6; MPN DMG6402LVT-7; Digikey_Part_Number DMG6402LVT-7DICT-ND; not fitted
R1, R2: 1K; R_1210_3225Metric; MPN CRCW12101K00JNEAIF
R3, R4, R5: 10K; R_0603_1608Metric; MPN RMCF0603JT10K0; Digikey_Part_Number RMCF0603JT10K0CT-ND
R6, R7, R8: 0R; R_0603_1608Metric; MPN RMCF0603ZT0R00; Digikey_Part_Number RMCF0603ZT0R00CT-ND
R9, R10, R11: 0R; R_0603_1608Metric; MPN RMCF0603ZT0R00; Digikey_Part_Number RMCF0603ZT0R00CT-ND; not fitted

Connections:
+3V3: J11.1, J13.1 (+3.3V), J13.2 (+3.3V), J13.12 (+3.3V), J13.13 (+3.3V)
+5V: J1.3, J8.1, J9.1, J11.17, J13.4 (+5V), J13.6 (+5V), J13.21 (+5V), J13.22 (+5V), J13.23 (+5V)
+12V: J3.3, J4.3, J5.3, J6.3, J10.1, J13.10 (+12V), J13.11 (+12V)
/A1: J2.6, J11.4
/AO: J2.5, J11.2
/BUTTON_1: J1.8, J11.5
/BUTTON_2: J1.9, J11.7
/BUTTON_3: J1.10, J11.9
/IO12: J1.5, J11.8
/IO13: J1.4, J11.6
/MISO: J2.13, J11.14, R6.2
/MOSI: J2.12, J11.12, R7.2
/PS_ON: J12.1, J13.16 (PS_ON#)
/PWM_FAN_IN_1: J5.1, R7.1, R10.1
/PWM_FAN_IN_2: J6.1, R6.1, R11.1
/PWM_L: Q3.3 (G), R5.1, R8.1, R9.1
/SCK: J2.11, J11.10, R8.2
/SCL: J1.12, J11.15
/SDA: J1.11, J11.13
/TACH_1: J2.16, J5.2, R1.2
/TACH_2: J2.10, J6.2, R2.2
/TOGGLE_COOL_1: J1.6, Q1.3 (G), Q4.3 (G), R3.1
/TOGGLE_COOL_2: J1.7, Q2.3 (G), Q5.3 (G), R4.1
GND: J2.4, J5.4, J6.4, J11.3, J11.19, J12.2, J13.3 (GND), J13.5 (GND), J13.7 (GND), J13.15 (GND), J13.17 (GND), J13.18 (GND), J13.19 (GND), J13.24 (GND), Q1.4 (S), Q2.4 (S), Q3.4 (S), Q4.4 (S), Q5.4 (S), Q6.4 (S), Q7.4 (S), R3.2, R4.2, R5.2
unnamed: J2.7, R9.2
unnamed: J2.8, R10.2
unnamed: J2.9, R11.2
unnamed: J3.4, Q1.1 (D), Q1.2 (D), Q1.5 (D), Q1.6 (D)
unnamed: J4.4, Q2.1 (D), Q2.2 (D), Q2.5 (D), Q2.6 (D)
unnamed: J8.2, Q4.1 (D), Q4.2 (D), Q4.5 (D), Q4.6 (D)
unnamed: J9.2, Q5.1 (D), Q5.2 (D), Q5.5 (D), Q5.6 (D)
unnamed: J10.2, Q3.1 (D), Q3.2 (D), Q3.5 (D), Q3.6 (D)
unnamed: J10.3, Q6.1 (D), Q6.2 (D), Q6.5 (D), Q6.6 (D)
unnamed: J10.4, Q7.1 (D), Q7.2 (D), Q7.5 (D), Q7.6 (D)
VCC: J2.2, R1.1, R2.1

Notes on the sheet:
Aux Board (for remote display)
Fans
ATX Power supply
DO NOT USE. RX/TX tied to this line.
See OLED display to verify pin<->button mapping
Main board
Cable adapter
Pin cannot be pulled high during boot ToDo: Add source for this comment
Lights
Future I2C expansion
Main Board
1. We can have a provion in the AUX board using jumpers to either use the buttons on the display OR use other buttons 2. See product link below for OLED wing
Ribbon cable
Custon cable with just power rails
Temp Sensor
Aux board
PELTIER
PWM_CONTROL
LINK:Or buy this
BUTTON_B
See image for the truth source
Aux Board - for a separate display
MCU connections
LINK: Check pinout here
4 pin connector options 1. 0022232041 (plastic shroud looks like is on 4 pins) 2. 0022292041 (plastic shroud looks like is on 4 pins) We need plastic shroud on 3 pins 1. 0470533000 - this option should work, BUT, it has a post. That makes it a non-std footprint, which i dont want to deal with - Let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
GND
Mosfets: https://www.digikey.com/en/products/detail/diodes-incorporated/DMG6402LDM-7/2179845 https://www.digikey.com/en/products/detail/vishay-siliconix/IRLZ14PBF/811728
BUTTON_C
ToDo: Explicitely mark pins as "free to use". Helps future designers to allocate Pins when the design expands.
OUTSIDE FANS 1. ON when Peltier is powered ON 2. OFF when Peltier is powered OFF
OLED wing https://www.adafruit.com/product/4650
Currently we only need 2 pin. But, adding a 4 pin to potentially support a RGB control (R+G+B+GND)
ATX connector
INSIDE FANS 1. Always powered ON, but speed controlled through PWM signal
Pin mapping can be verfied in software: https://github.com/nitin710/openplant_incubator_fw
ToDo: verify the polarity of the connector. The pin nets change depending on the perspective (Looking from back or front)
LIGHTS
+5VSB (STAND_BY)
BUTTON_A
FANS

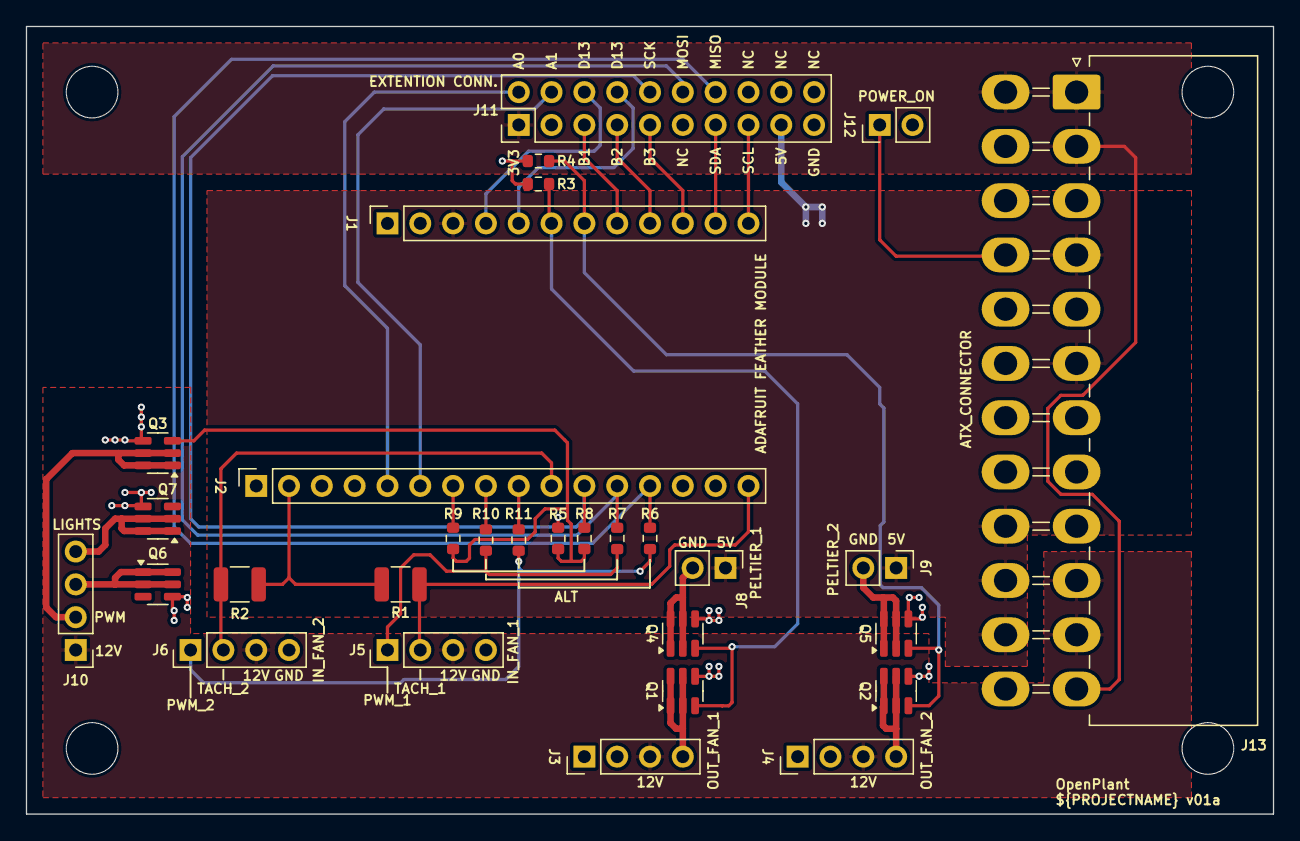
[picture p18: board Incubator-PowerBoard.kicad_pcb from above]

Board: 2 copper layers, 96.5 x 61.0 mm, 30 parts (0 on the bottom side), 35 nets.

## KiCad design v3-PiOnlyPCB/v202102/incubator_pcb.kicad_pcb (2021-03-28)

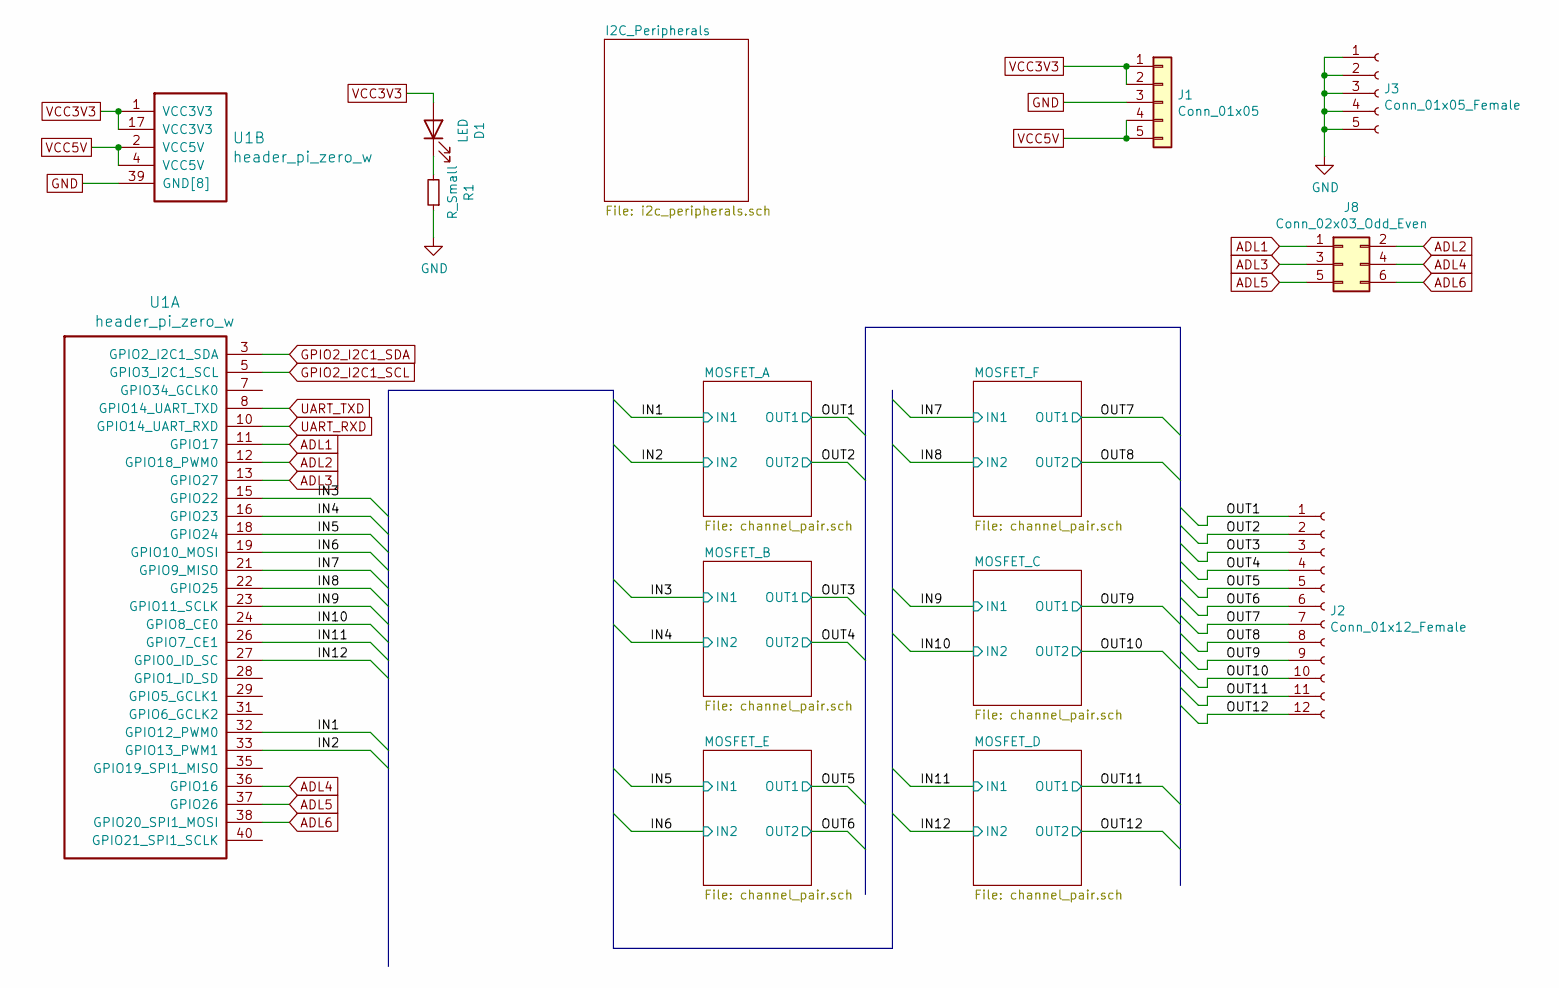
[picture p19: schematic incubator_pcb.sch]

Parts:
D1: LED; D_0805_2012Metric_Pad1.15x1.40mm_HandSolder
J1: Conn_01x05; PinHeader_1x05_P2.54mm_Vertical
J2: Conn_01x12_Female; PWRCON_3M81-12
J3: Conn_01x05_Female; PWRCON_3M81-5
J8: Conn_02x03_Odd_Even; PinHeader_2x03_P2.54mm_Vertical
R1: R_Small; R_0805_2012Metric_Pad1.20x1.40mm_HandSolder
U1: header_pi_zero_w; PinHeader_2x20_P2.54mm_Vertical

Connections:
/IN1: U1.32 (GPIO12_PWM0); also elsewhere on the board
/IN2: U1.33 (GPIO13_PWM1); also elsewhere on the board
/IN3: U1.15 (GPIO22); also elsewhere on the board
/IN4: U1.16 (GPIO23); also elsewhere on the board
/IN5: U1.18 (GPIO24); also elsewhere on the board
/IN6: U1.19 (GPIO10_MOSI); also elsewhere on the board
/IN7: U1.21 (GPIO9_MISO); also elsewhere on the board
/IN8: U1.22 (GPIO25); also elsewhere on the board
/IN9: U1.23 (GPIO11_SCLK); also elsewhere on the board
/IN10: U1.24 (GPIO8_CE0); also elsewhere on the board
/IN11: U1.26 (GPIO7_CE1); also elsewhere on the board
/IN12: U1.27 (GPIO0_ID_SC); also elsewhere on the board
/OUT1: J2.1; also elsewhere on the board
/OUT2: J2.2; also elsewhere on the board
/OUT3: J2.3; also elsewhere on the board
/OUT4: J2.4; also elsewhere on the board
/OUT5: J2.5; also elsewhere on the board
/OUT6: J2.6; also elsewhere on the board
/OUT7: J2.7; also elsewhere on the board
/OUT8: J2.8; also elsewhere on the board
/OUT9: J2.9; also elsewhere on the board
/OUT10: J2.10; also elsewhere on the board
/OUT11: J2.11; also elsewhere on the board
/OUT12: J2.12; also elsewhere on the board
ADL1: J8.1, U1.11 (GPIO17)
ADL2: J8.2, U1.12 (GPIO18_PWM0)
ADL3: J8.3, U1.13 (GPIO27)
ADL4: J8.4, U1.36 (GPIO16)
ADL5: J8.5, U1.37 (GPIO26)
ADL6: J8.6, U1.38 (GPIO20_SPI1_MOSI)
GND: J1.3, J3.1, J3.2, J3.3, J3.4, J3.5, R1.1, U1.6 (GND[8]), U1.9 (GND[8]), U1.14 (GND[8]), U1.20 (GND[8]), U1.25 (GND[8]), U1.30 (GND[8]), U1.34 (GND[8]), U1.39 (GND[8]); also elsewhere on the board
GPIO2_I2C1_SCL: U1.5 (GPIO3_I2C1_SCL); also elsewhere on the board
GPIO2_I2C1_SDA: U1.3 (GPIO2_I2C1_SDA); also elsewhere on the board
unnamed: D1.1 (K), R1.2
VCC3V3: D1.2 (A), J1.1, J1.2, U1.1 (VCC3V3), U1.17 (VCC3V3); also elsewhere on the board
VCC5V: J1.4, J1.5, U1.2 (VCC5V), U1.4 (VCC5V)

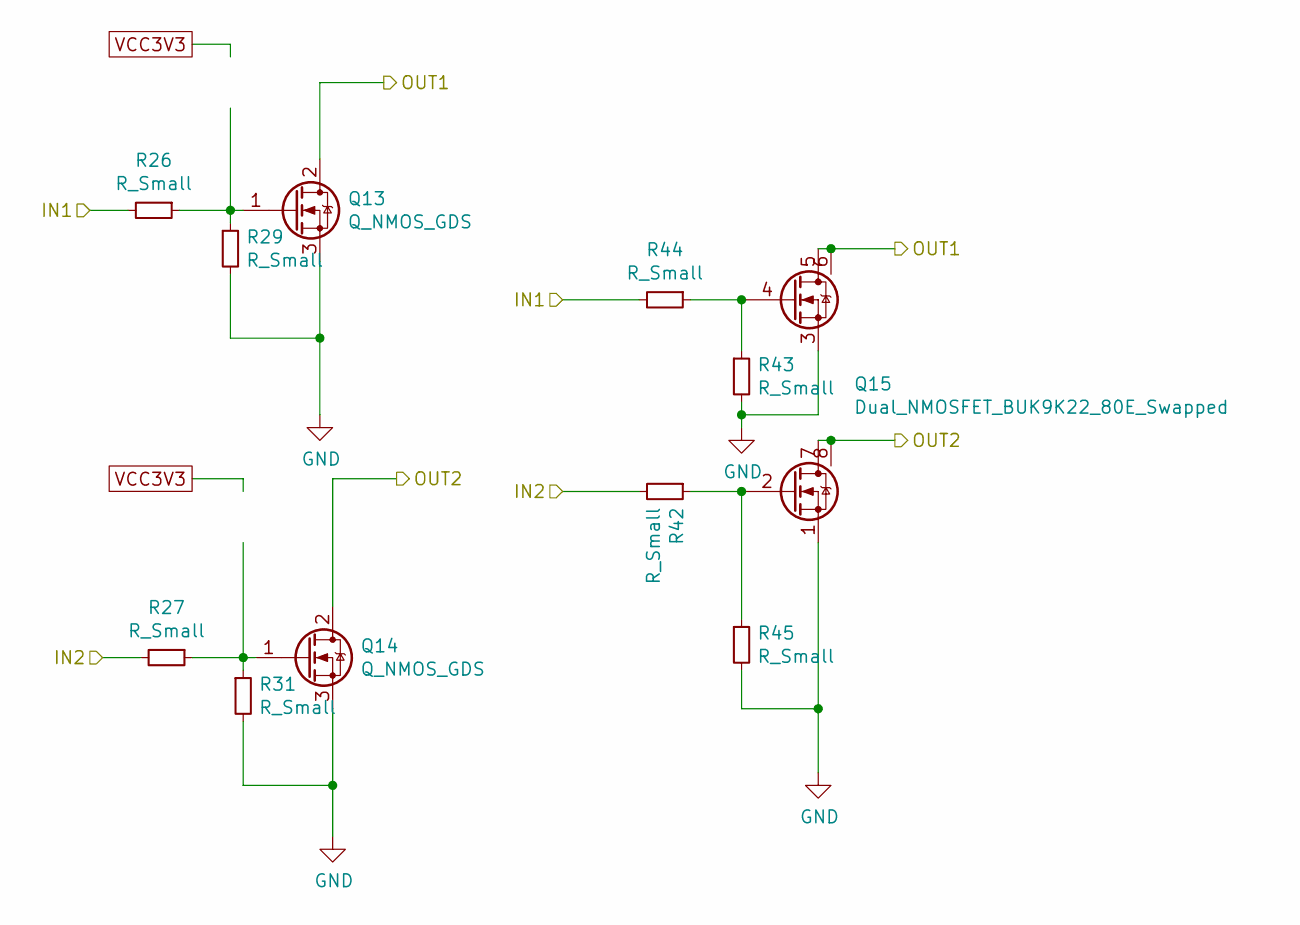
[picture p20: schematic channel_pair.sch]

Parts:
Q1, Q2: Q_NMOS_GDS; TO-252-2
Q3: Dual_NMOSFET_BUK9K22_80E_Swapped; LFPAK56D
R2, R3, R4, R5, R6, R7, R10, R12: R_Small; R_0805_2012Metric_Pad1.20x1.40mm_HandSolder

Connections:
/IN1: R2.2, R10.2; also elsewhere on the board
/IN2: R3.2, R4.2; also elsewhere on the board
/OUT1: Q1.2 (D), Q3.5 (D1), Q3.6 (D1); also elsewhere on the board
/OUT2: Q2.2 (D), Q3.7 (D2), Q3.8 (D2); also elsewhere on the board
GND: Q1.3 (S), Q2.3 (S), Q3.1 (S2), Q3.3 (S1), R5.2, R6.2, R7.2, R12.2; also elsewhere on the board
unnamed: Q1.1 (G), R2.1, R5.1
unnamed: Q2.1 (G), R3.1, R7.1
unnamed: Q3.2 (G2), R4.1, R12.1
unnamed: Q3.4 (G1), R6.1, R10.1

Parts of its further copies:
Q4, Q5, Q7, Q8, Q10, Q11, Q13, Q14, Q16, Q17: Q_NMOS_GDS; TO-252-2
Q6, Q9, Q12, Q15, Q18: Dual_NMOSFET_BUK9K22_80E_Swapped; LFPAK56D
R8, R9, R11, R13, R14, R15, R16, R17, R18, R19, R20, R21, R22, R23, R24, R25, R26, R27, R28, R29, R30, R31, R32, R33, R34, R35, R36, R37, R38, R39, R40, R41, R42, R43, R44, R45, R46, R47, R48, R49: R_Small; R_0805_2012Metric_Pad1.20x1.40mm_HandSolder

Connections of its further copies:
/IN3: R8.2, R22.2; also elsewhere on the board
/IN4: R9.2, R16.2; also elsewhere on the board
/IN5: R26.2, R44.2; also elsewhere on the board
/IN6: R27.2, R42.2; also elsewhere on the board
/IN7: R32.2, R48.2; also elsewhere on the board
/IN8: R33.2, R46.2; also elsewhere on the board
/IN9: R14.2, R34.2; also elsewhere on the board
/IN10: R15.2, R28.2; also elsewhere on the board
/IN11: R20.2, R40.2; also elsewhere on the board
/IN12: R21.2, R38.2; also elsewhere on the board
/OUT3: Q4.2 (D), Q6.5 (D1), Q6.6 (D1); also elsewhere on the board
/OUT4: Q5.2 (D), Q6.7 (D2), Q6.8 (D2); also elsewhere on the board
/OUT5: Q13.2 (D), Q15.5 (D1), Q15.6 (D1); also elsewhere on the board
/OUT6: Q14.2 (D), Q15.7 (D2), Q15.8 (D2); also elsewhere on the board
/OUT7: Q16.2 (D), Q18.5 (D1), Q18.6 (D1); also elsewhere on the board
/OUT8: Q17.2 (D), Q18.7 (D2), Q18.8 (D2); also elsewhere on the board
/OUT9: Q7.2 (D), Q9.5 (D1), Q9.6 (D1); also elsewhere on the board
/OUT10: Q8.2 (D), Q9.7 (D2), Q9.8 (D2); also elsewhere on the board
/OUT11: Q10.2 (D), Q12.5 (D1), Q12.6 (D1); also elsewhere on the board
/OUT12: Q11.2 (D), Q12.7 (D2), Q12.8 (D2); also elsewhere on the board
GND: Q4.3 (S), Q5.3 (S), Q6.1 (S2), Q6.3 (S1), Q7.3 (S), Q8.3 (S), Q9.1 (S2), Q9.3 (S1), Q10.3 (S), Q11.3 (S), Q12.1 (S2), Q12.3 (S1), Q13.3 (S), Q14.3 (S), Q15.1 (S2), Q15.3 (S1), Q16.3 (S), Q17.3 (S), Q18.1 (S2), Q18.3 (S1), R11.2, R13.2, R17.2, R18.2, R19.2, R23.2, R24.2, R25.2, R29.2, R30.2, R31.2, R35.2, R36.2, R37.2, R39.2, R41.2, R43.2, R45.2, R47.2, R49.2; also elsewhere on the board
unnamed: Q4.1 (G), R8.1, R11.1
unnamed: Q5.1 (G), R9.1, R13.1
unnamed: Q6.2 (G2), R16.1, R24.1
unnamed: Q6.4 (G1), R18.1, R22.1
unnamed: Q7.1 (G), R14.1, R17.1
unnamed: Q8.1 (G), R15.1, R19.1
unnamed: Q9.2 (G2), R28.1, R36.1
unnamed: Q9.4 (G1), R30.1, R34.1
unnamed: Q10.1 (G), R20.1, R23.1
unnamed: Q11.1 (G), R21.1, R25.1
unnamed: Q12.2 (G2), R38.1, R41.1
unnamed: Q12.4 (G1), R39.1, R40.1
unnamed: Q13.1 (G), R26.1, R29.1
unnamed: Q14.1 (G), R27.1, R31.1
unnamed: Q15.2 (G2), R42.1, R45.1
unnamed: Q15.4 (G1), R43.1, R44.1
unnamed: Q16.1 (G), R32.1, R35.1
unnamed: Q17.1 (G), R33.1, R37.1
unnamed: Q18.2 (G2), R46.1, R49.1
unnamed: Q18.4 (G1), R47.1, R48.1

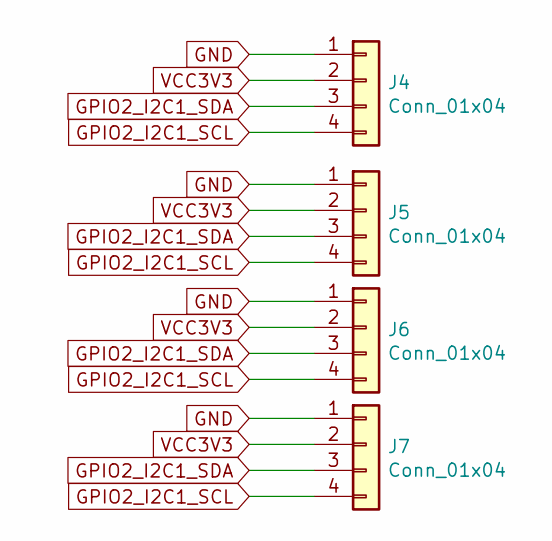
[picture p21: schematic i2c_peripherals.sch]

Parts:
J4, J5: Conn_01x04; JST_SH_BM04B-SRSS-TB_1x04-1MP_P1.00mm_Vertical
J6, J7: Conn_01x04; PinHeader_1x04_P2.54mm_Vertical

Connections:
GND: J4.1, J5.1, J6.1, J7.1; also elsewhere on the board
GPIO2_I2C1_SCL: J4.4, J5.4, J6.4, J7.4; also elsewhere on the board
GPIO2_I2C1_SDA: J4.3, J5.3, J6.3, J7.3; also elsewhere on the board
VCC3V3: J4.2, J5.2, J6.2, J7.2; also elsewhere on the board

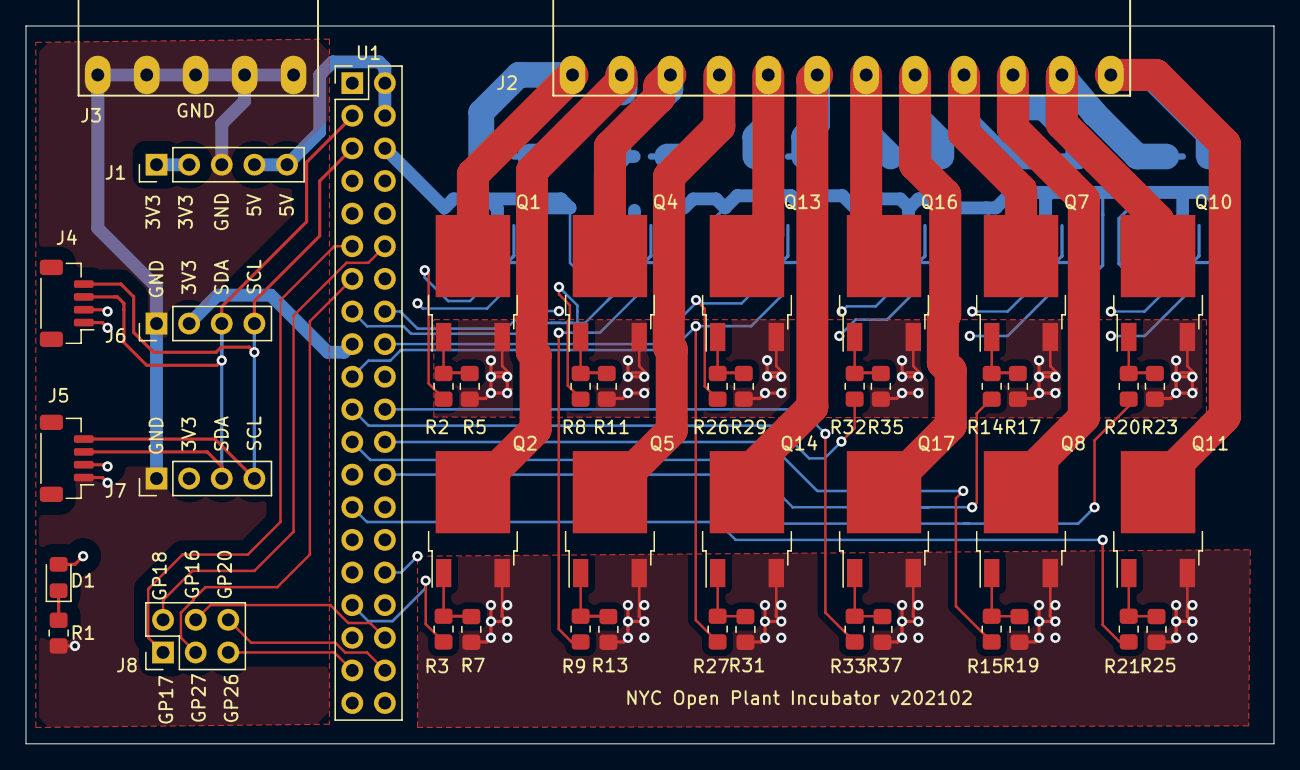
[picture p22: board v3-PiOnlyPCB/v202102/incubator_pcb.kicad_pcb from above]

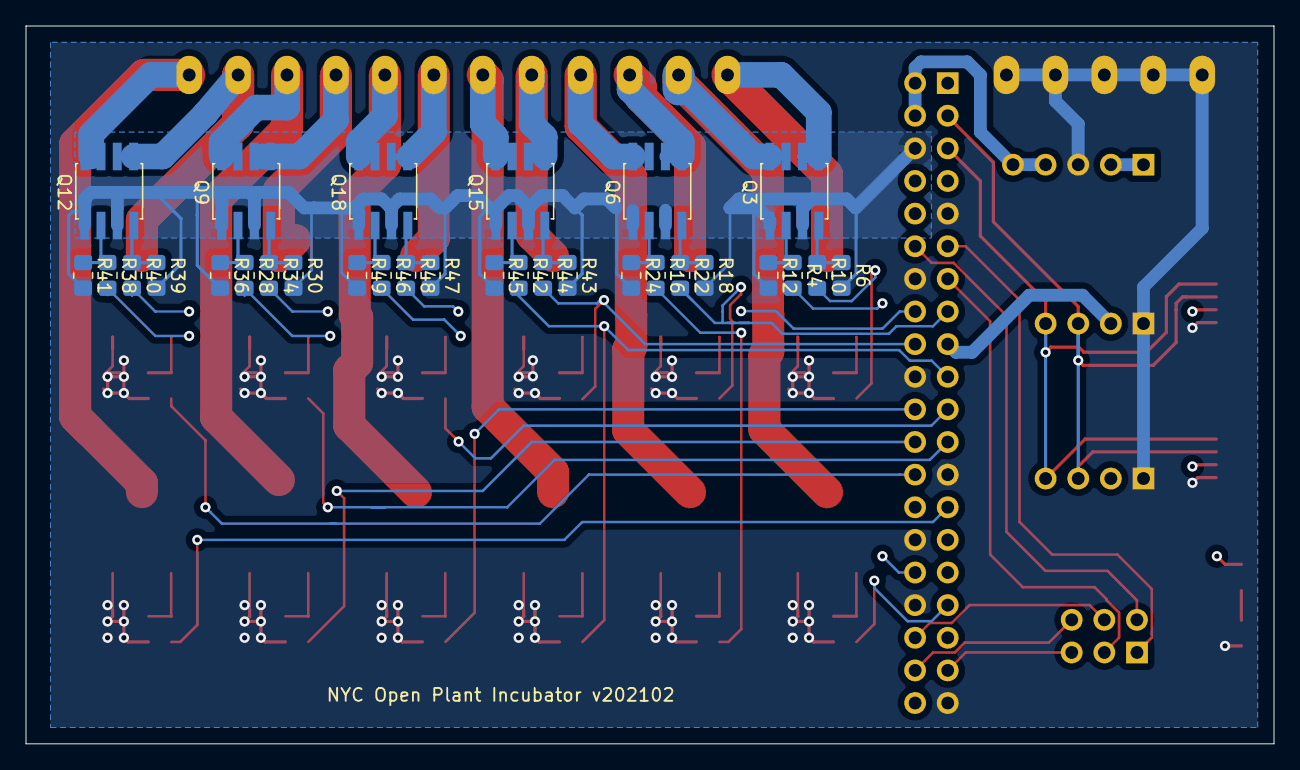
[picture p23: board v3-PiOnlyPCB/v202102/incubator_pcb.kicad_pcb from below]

Board: 4 copper layers, 97.2 x 55.9 mm, 77 parts (30 on the bottom side), 60 nets.

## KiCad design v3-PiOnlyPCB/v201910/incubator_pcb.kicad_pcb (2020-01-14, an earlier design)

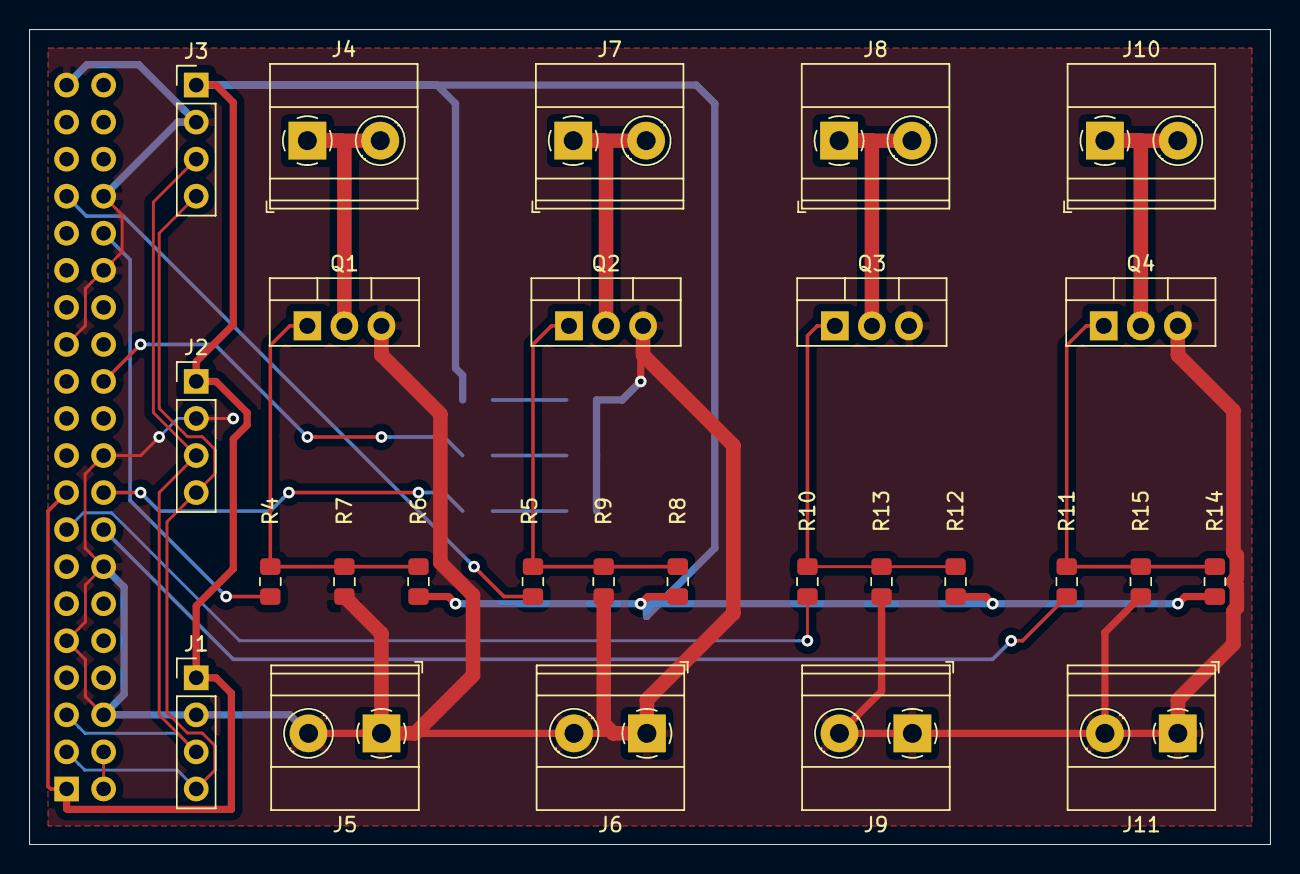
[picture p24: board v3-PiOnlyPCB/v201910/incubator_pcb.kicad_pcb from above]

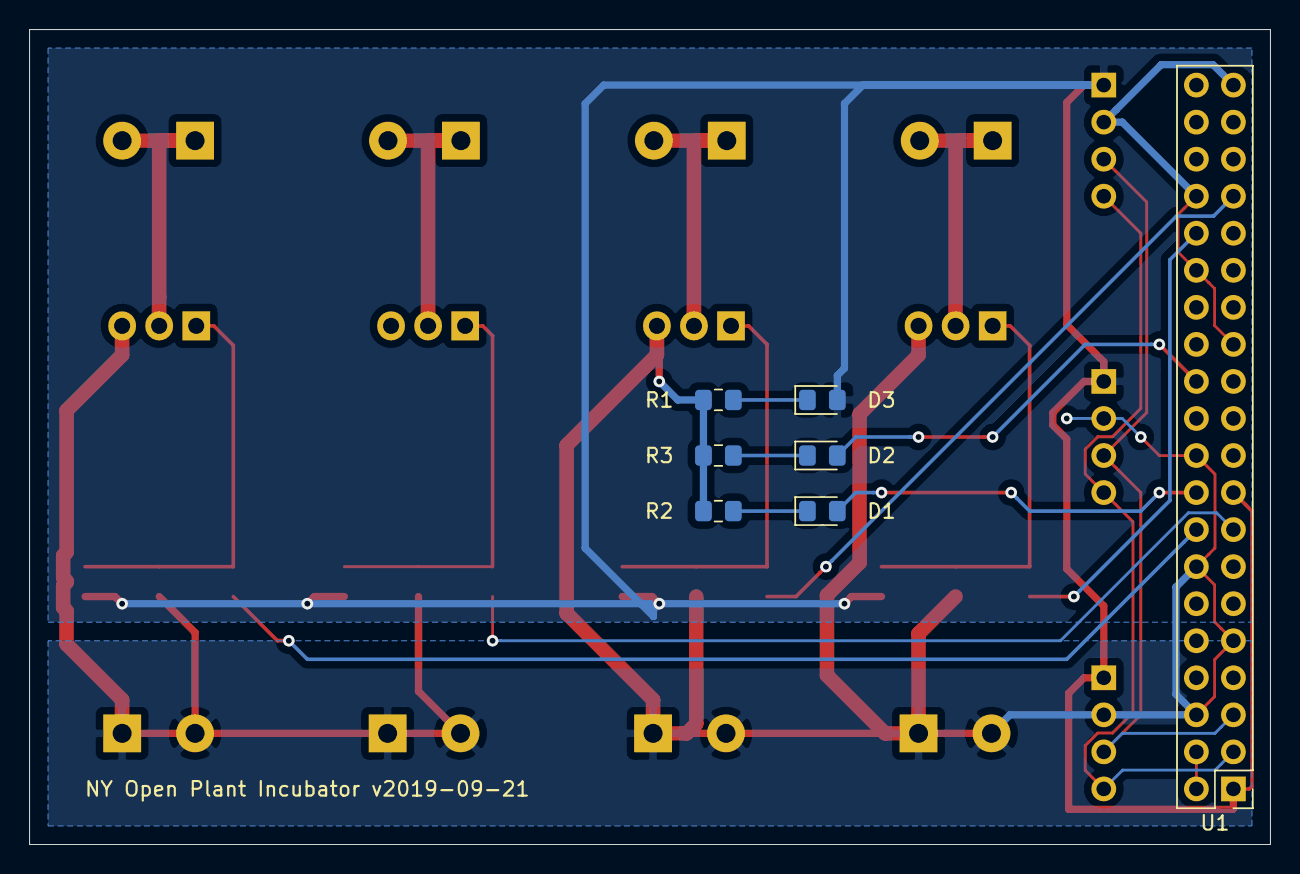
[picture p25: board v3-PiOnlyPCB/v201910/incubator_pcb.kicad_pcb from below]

Board: 2 copper layers, 85.1 x 55.9 mm, 34 parts (7 on the bottom side), 22 nets.

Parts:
D1, D2, D3: LED; D_0805_2012Metric_Pad1.15x1.40mm_HandSolder
J1, J2, J3: Conn_01x04; PinHeader_1x04_P2.54mm_Vertical
J4, J5, J6, J7, J8, J9, J10, J11: Conn_01x02; TerminalBlock_Phoenix_MKDS-1,5-2_1x02_P5.00mm_Horizontal
Q1, Q2, Q3, Q4: Q_NMOS_GDS; TO-220-3_Vertical
R1, R2, R3, R4, R5, R6, R7, R8, R9, R10, R11, R12, R13, R14, R15: R_Small; R_0805_2012Metric_Pad1.15x1.40mm_HandSolder
U1: header_pi_zero_w; PinHeader_2x20_P2.54mm_Vertical

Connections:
GND: J1.2, J2.2, J3.2, J5.1, J5.2, J6.1, J6.2, J9.1, J9.2, J11.1, J11.2, Q1.3, Q2.3, Q3.3, Q4.3, R1.1, R2.1, R3.1, R7.2, R9.2, R13.2, R15.2, U1.6, U1.9, U1.14, U1.20, U1.25, U1.30, U1.34, U1.39
GPIO2_I2C1_SCL: J1.3, J2.3, J3.3, U1.5
GPIO2_I2C1_SDA: J1.4, J2.4, J3.4, U1.3
GPIO12_PWM0: R4.2, U1.32
GPIO13_PWM1: R5.2, U1.33
GPIO22: R10.2, U1.15
GPIO23: R11.2, U1.16
unnamed: D1.1, R2.2
unnamed: D1.2, U1.18
unnamed: D2.1, R3.2
unnamed: D2.2, U1.24
unnamed: D3.1, R1.2
unnamed: J4.1, J4.2, Q1.2
unnamed: J7.1, J7.2, Q2.2
unnamed: J8.1, J8.2, Q3.2
unnamed: J10.1, J10.2, Q4.2
unnamed: Q1.1, R4.1, R6.2, R7.1
unnamed: Q2.1, R5.1, R8.2, R9.1
unnamed: Q3.1, R10.1, R12.2, R13.1
unnamed: Q4.1, R11.1, R14.2, R15.1
VCC3V3: D3.2, J1.1, J2.1, J3.1, R6.1, R8.1, R12.1, R14.1, U1.1, U1.17
VCC5V: U1.2, U1.4

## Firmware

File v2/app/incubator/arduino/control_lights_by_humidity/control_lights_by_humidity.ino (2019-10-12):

/***************************************************
  This is an test program to verify the wiring is correct. 
  If the humidity above 60% the lights and Peltier turn on. 
  You can trigger this by putting a finger on the humidty sensor.

  Designed specifically to work with the SHT31-D sensor from Adafruit
  ----> https://www.adafruit.com/products/2857

  These sensors use I2C to communicate, 2 pins are required to
  interface

  Wired the SHT31-D to the Arduino following the first diagram here:
  http://cactus.io/hookups/sensors/temperature-humidity/sht31/hookup-arduino-to-sensirion-sht31-temp-humidity-sensor

  Connect the LED strip to the gate following the diagram in the Cloud-based Lab Monitor google doc:
  Power Supply - to breadboard minus rail
  Power Supply + to LED strip red wire
  LED strip black wire to gate middle pin

  The small LED does not light up because when the humidity sensor is connected, the Arduino 
  does not have enough power to power it.
 ****************************************************/

#include <Arduino.h>
#include <Wire.h>
#include "Adafruit_SHT31.h"

const int lights = 4;
const int peltier = 5;
const int ledPin = LED_BUILTIN;// the number of the LED pin, this is pin 13 for the LED
const int humidityThreshold = 60.0;

int ledState = LOW;
int ledStripState = LOW;
int peltierState = LOW;

/*
  This next section defines a a subclass of the tempurature sensing
  hardware as Tempsensor which will hold the information from the last
  time the sensor was polled

*/

class Tempsensor: public Adafruit_SHT31 {
  private:
    byte readInterval;            // the time in seconds between readings
    unsigned long lastUpdate;     // to store the millis

  public:
    float temp;                   // to store the tempurature data
    float humidity;               // to store the humidity data

    /*
      Constructor, also should call the base class constructor

    */

    Tempsensor(byte seconds) {
      readInterval = seconds;
      temp = 0;
      humidity = 0;
      lastUpdate = millis();
    }

    void Update() {
      unsigned long currentMillis = millis();

      if ((currentMillis - lastUpdate) >= (readInterval * 1000)) {
        lastUpdate = millis();
        temp = readTemperature();
        humidity = readHumidity();
      }
      if (humidity > humidityThreshold) {
        if (ledState == LOW) {
          ledState = HIGH;
          Serial.println("Humidity is >= " + String(humidityThreshold) + ", turning small LED on");
          digitalWrite(ledPin, ledState);
        }
        if (ledStripState == LOW) {
          ledStripState = HIGH;
          Serial.println("Humidity is >= " + String(humidityThreshold) + ", turning LED strip on");
          digitalWrite(lights, ledStripState);
        }
        if (peltierState == LOW) {
          peltierState = HIGH;
          Serial.println("Humidity is >= " + String(humidityThreshold) + ", turning Peltier on");
          digitalWrite(peltier, peltierState);
        }
      }
      else {
        if (ledState == HIGH) {
          ledState = LOW;
          Serial.println("Humidity is < " + String(humidityThreshold) + ", turning small LED off");
          digitalWrite(ledPin, ledState);
        }
        if (ledStripState == HIGH) {
          ledStripState = LOW;
          Serial.println("Humidity is < " + String(humidityThreshold) + ", turning LED strip off");
          digitalWrite(lights, ledStripState);
        }
        if (peltierState == HIGH) {
          peltierState = LOW;
          Serial.println("Humidity is < " + String(humidityThreshold) + ", turning Peltier off");
          digitalWrite(peltier, peltierState);
        }
      }
    }

    void testprint() {
      unsigned long currentMillis = millis();

      if ((currentMillis - lastUpdate) >= (readInterval * 1000)) {
        Serial.print("Current millis() = "); Serial.println(currentMillis);
        Serial.print("Millis of last poll = "); Serial.println(lastUpdate);
        Serial.print("Temp *C = "); Serial.println(temp);
        Serial.print("Hum. % = "); Serial.println(humidity);
        Serial.println();
      }
    }

    void TestLight() {
      unsigned long currentMillis = millis();

      if ((currentMillis - lastUpdate) >= (readInterval * 1000)) {
        lastUpdate = millis();
        if (ledState == LOW) {
          ledState = HIGH;
          Serial.println("turning LED on");
        } else {
          ledState = LOW;
          Serial.println("turning LED off");
        }
    
        // set the LED with the ledState of the variable:
        digitalWrite(ledPin, ledState);
      }
    }
};

Tempsensor testsensor = Tempsensor(2); // initialize the sensor

void setup() {

  /*
    Set the pins which are attached to other devices to output to
    prevent a floating pin which can casues issues

  */
  pinMode(3, OUTPUT);
  pinMode(lights, OUTPUT);
  pinMode(peltier, OUTPUT);

  Serial.begin(9600);

  if (! testsensor.begin()) {   // Set to 0x45 for alternate i2c addr
    Serial.println("Couldn't find SHT31");
    while (1);
  }
  Serial.println("setup successful");
}


void loop() {

  testsensor.testprint();
  testsensor.Update();
//  testsensor.TestLight();
}

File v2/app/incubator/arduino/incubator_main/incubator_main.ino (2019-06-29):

/***************************************************
  This is the main file to control the incubator. Rewritten from Danny's prototype_incubator.ino

  Designed specifically to work with the SHT31-D sensor from Adafruit
  ----> https://www.adafruit.com/products/2857

  Wired the SHT31-D to the Arduino following the first diagram here:
  http://cactus.io/hookups/sensors/temperature-humidity/sht31/hookup-arduino-to-sensirion-sht31-temp-humidity-sensor

  Connect the LED strip to the MOSFET transistor following the diagram in the Cloud-based Lab Monitor google doc:
  Power Supply - to breadboard minus rail
  Power Supply + to LED strip red wire
  LED strip black wire to gate middle pin
 ****************************************************/

#include "Adafruit_SHT31.h"
#include "RTClib.h"           // library for the RTC

const float peltier_on_threshold = 25.0;
const float peltier_off_threshold = 24.0;

const int fan = 3;  // we just run the fans constantly with no input or output, as Danny did
const int lights = 4;
const int peltier = 5;

int peltierState = LOW;

Adafruit_SHT31 sht31 = Adafruit_SHT31();  // name the temp sensor
RTC_PCF8523 rtc;                          // name the clock

void setup() {
  /*
    Set the pins which are attached to other devices to output to
    prevent a floating pin which can cause issues

  */
  pinMode(fan, OUTPUT);
  pinMode(lights, OUTPUT);
  pinMode(peltier, OUTPUT);

  Serial.begin(9600);
  
  /* set up temp sensor */
  if (! sht31.begin(0x44)) {   // Set to 0x45 for alternate i2c addr
    Serial.println("Couldn't find SHT31");
    while (1) delay(1);
  }
  
  Serial.println("setup successful");
}

DateTime getCurrentTime() {
  return rtc.now();
}

void printCurrentData(DateTime currentTime, float currentTemp, float currentHum) {
  Serial.print("The clock is set to: "); 
  Serial.print(currentTime.hour()); 
  Serial.print(':'); 
  Serial.print(currentTime.minute()); 
  Serial.print(':'); 
  Serial.print(currentTime.second());
  Serial.print(" on "); 
  Serial.print(currentTime.year(), DEC); 
  Serial.print('/'); 
  Serial.print(currentTime.month(), DEC); 
  Serial.print('/'); 
  Serial.println(currentTime.day(), DEC);
  
  Serial.print("Temp *C = "); 
  Serial.println(currentTemp);

  Serial.print("Hum. % = "); 
  Serial.println(currentHum);
}

void recordCurrentData(DateTime currentTime, float currentTemp, float currentHum) {
  // TODO connect to raspberry pi and save the data somewhere in the cloud
}

void adjustPeltier(float currentTemp) {
  // TODO(low priority) replace with a smarter algorithm, use PID like Danny
  if (currentTemp > peltier_on_threshold) {
    peltierState = HIGH;
    Serial.println("Current temperature " + String(currentTemp) + " is higher than " + String(peltier_on_threshold) + ", turning Peltier cooler on");
    digitalWrite(peltier, peltierState);
  }
  else if (currentTemp < peltier_off_threshold) {
    peltierState = LOW;
    Serial.println("Current temperature " + String(currentTemp) + " is lower than " + String(peltier_off_threshold) + ", turning Peltier cooler off");
    digitalWrite(peltier, peltierState);
  }
  if (peltierState == HIGH) {
    Serial.println("Peltier is on");
  } else if (peltierState == LOW) {
    Serial.println("Peltier is off");
  }
}

void adjustLight(DateTime currentTime) {
  int hour = currentTime.hour();
  if (hour >= 4 && hour < 12) {
    digitalWrite(lights, LOW);
    Serial.println("Time is between 4am-12pm - lights are off");
  }
  else {
    digitalWrite(lights, HIGH);
    Serial.println("Time is between 12pm-4am - lights are on");
  }
}

void loop() {
  DateTime currentTime = getCurrentTime();
  float currentTemp = sht31.readTemperature();
  float currentHum = sht31.readHumidity();
  printCurrentData(currentTime, currentTemp, currentHum);
  recordCurrentData(currentTime, currentTemp, currentHum);

  adjustPeltier(currentTemp);
  adjustLight(currentTime);

  delay(5000);
}

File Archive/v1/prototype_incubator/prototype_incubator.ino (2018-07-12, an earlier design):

#include <PID_v1.h>               // library for the PID
#include "Adafruit_SHT31.h"       // library for the tempurature sensor
#include <Adafruit_Sensor.h>      // unified sensor library
#include <Adafruit_TSL2561_U.h>   // library for the light sensor
#include <SPI.h>                  // library for the pins the SD card is using
#include <SD.h>                   // library for the SD card
#include <Wire.h>
#include "RTClib.h"               // library for the RTC

/* Set the appropriate digital I/O pin connections. These are the pin */

const int chipSelect = 10; // set the pin for the SD card

const int lights = 4;   // pin for the lights
const int peltier = 5;  // PWM pin for the peltier
const int fan = 3;      // PWM pin for the fan

//const int innerSensefan = 8;  // Sensor for the inner fan speed
//const int outerSensefan = 7;  // Sensor for the outer fan speed

/* define the sensors */

RTC_PCF8523 rtc;                                                                        // name the clock
Adafruit_TSL2561_Unified tsl = Adafruit_TSL2561_Unified(TSL2561_ADDR_FLOAT, 12345);     // name the lux sensor
Adafruit_SHT31 sht31 = Adafruit_SHT31();                                                // name the temp sensor

// char daysOfTheWeek[7][12] = {"Sunday", "Monday", "Tuesday", "Wednesday", "Thursday", "Friday", "Saturday"};
/* The array os string used to store the data as it comes from the sensors */

/* PID variables and constants */
double Setpoint, Input, Output=255;

//Define the Tuning Parameters foir when the light is on and when it is off
const double lightKp=150, lightKi=20, lightKd=1;
//const double darkKp=50, darkKi=10, darkKd=15;

//Specify the links and initial tuning parameters
PID myPID(&Input, &Output, &Setpoint, lightKp, lightKi, lightKd, REVERSE);

/* Setpoints */

//const int luxSet = 50;
const int tempSet = 21;

/**************************************************************************/
/*
    Configures the gain and integration time for the TSL2561
*/
/**************************************************************************/
void configureLux(void)
{ 
  /* You can also manually set the gain or enable auto-gain support */
  // tsl.setGain(TSL2561_GAIN_1X);      /* No gain ... use in bright light to avoid sensor saturation */
  // tsl.setGain(TSL2561_GAIN_16X);     /* 16x gain ... use in low light to boost sensitivity */
  tsl.enableAutoRange(true);            /* Auto-gain ... switches automatically between 1x and 16x */
  
  /* Changing the integration time gives you better sensor resolution (402ms = 16-bit data) */
  // tsl.setIntegrationTime(TSL2561_INTEGRATIONTIME_13MS);      /* fast but low resolution */
  tsl.setIntegrationTime(TSL2561_INTEGRATIONTIME_101MS);  /* medium resolution and speed   */
  // tsl.setIntegrationTime(TSL2561_INTEGRATIONTIME_402MS);  /* 16-bit data but slowest conversions */
}

void configureSD() {
  // see if the card is present and can be initialized:
  if (!SD.begin(chipSelect)) {
    Serial.println("Card failed, or not present");
    // don't do anything more:
    while (1);
  }
}

String timeString() {
  DateTime now = rtc.now();
  char buffer[18];
  snprintf(buffer, 18, "%04d%02d%02d_%02d:%02d:%02d", now.year(), now.month(), now.day(), now.hour(), now.minute(), now.second());
  return buffer;
}

/* not accurate
double fanSpeed(int fan) {
  unsigned long rise = pulseIn(fan, HIGH);
  unsigned long fall = pulseIn(fan, LOW);
  unsigned long total = rise + fall;
  double rpm = 1000000/2*total*60;
  return rpm;
}
*/

/**************************************************************************/
/*
    Setup code
*/
/**************************************************************************/

void setup() {

  /* set up the output pins */

  pinMode(lights, OUTPUT);
  pinMode(peltier, OUTPUT);

  /* set up the input pins */

  //pinMode(innerSensefan, INPUT_PULLUP);
  //pinMode(outerSensefan, INPUT_PULLUP);

  /* set up serial */
  Serial.begin(9600);

  while (!Serial)
    delay(10);     // will pause Zero, Leonardo, etc until serial console opens
   
  /* set up temp sensor */
  if (! sht31.begin(0x44)) {   // Set to 0x45 for alternate i2c addr
    Serial.println("Couldn't find SHT31");
    while (1) delay(1);
  }

  /* Initialise the lux sensor */
  //use tsl.begin() to default to Wire, 
  //tsl.begin(&Wire2) directs api to use Wire2, etc.
  if(!tsl.begin())
  {
    /* There was a problem detecting the TSL2561 ... check your connections */
    Serial.print("Ooops, no TSL2561 detected ... Check your wiring or I2C ADDR!");
    while(1);
  }
  
  /* Setup the lux sensor gain and integration time */
  configureLux();
        
  /* Setup the SD card */
  configureSD();

  /* adjust timer 2 to give pin 3 and 11 25kHz output*/
  TCCR2A = 0x23;
  TCCR2B = 0x09;  // select timer2 clock
  OCR2A = 79;  // aiming for 25kHz
  pinMode(fan, OUTPUT);
  OCR2B = 62;  // set the PWM duty cycle

  
  /*Display the time for sanity*/
  DateTime now = rtc.now();
  Serial.print("The clock is set to: "); Serial.print(now.hour()); Serial.print(':'); Serial.print(now.minute()); Serial.print(':'); Serial.print(now.second());
  Serial.print(" on "); Serial.print(now.year(), DEC); Serial.print('/'); Serial.print(now.month(), DEC); Serial.print('/'); Serial.println(now.day(), DEC);
  Serial.println("-------------------------------");
  Serial.println();
  
  /*initialize the variables the PID is linked to*/
  Input = tempSet;
  Setpoint = tempSet;

  /*turn the PID on*/
  myPID.SetMode(AUTOMATIC);
}
  
/**************************************************************************/
/*
    Main loop code
*/
/**************************************************************************/
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

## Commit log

2018-05-28 update before branch for alternate component
    [prototype_breadboard_2.fzz]
2018-05-28 first commit getting the new clock integrated into the system. PID not working.
    [prototype_breadboard_3.fzz]
2018-06-11 update the circuit diagram
    [prototype_breadboard_3.fzz]
2018-06-11 prepared the routing to get a better idea of how how to simplify the wiring
    [prototype_breadboard_3.fzz]
2018-06-15 more diagrams and changed the chipselect pin
    [liverwort_incubator_v1.fzz, prototype_breadboard_3.fzz]
2018-06-29 update tests
    [liverwort_incubator_v1.fzz]
2018-07-11 resolved merge conflict by preserving the commented out pins
    [liverwort_incubator_v1.fzz]
2018-07-11 clean up the file structre and names
    [prototype_breadboard.fzz, prototype_breadboard_2.fzz, prototype_breadboard_3.fzz]
2018-07-13 add pull down resistors and change chip select pin
    [liverwort_incubator_v1.fzz]
2019-02-11 use the local version
    [liverwort_incubator_v1_LOCAL_32405.fzz]
2019-06-29 Separating v1 and v2
    [liverwort_incubator_v1.fzz, liverwort_incubator_v1_LOCAL_32405.fzz, prototype_breadboard.fzz]
2019-08-17 Added camera code
2019-10-12 Test program to verify the wiring is correct.
2019-11-02 Update camera script
    Replaced placeholders with calls to env variables, and added code to delete pictures from pi
2019-11-03 Update Incubator Files
    Separated the incubator files by those on the arduino vs those on the pi
2019-11-10 Add sensor logging init
2019-11-10 Update start sensor logging
2019-11-10 Add logging to log sensor data
2019-11-10 Update sensor logging
2019-11-10 Add more sensor logging
2019-12-14 Add sleep time to log sensor
2020-01-06 Update sensor data script
2020-01-14 Add KiCad files for RaspberryPi only version 2019-10.
    [incubator_pcb.kicad_pcb, incubator_pcb.sch, pi_zero_w.csv]
2020-10-10 Add new raspberry scripts
2020-10-17 Add sensor record to log
2020-10-24 Add test camera script
2020-11-07 Update basic all to work without logging sensor value to database if I2C not enabled
2020-11-23 Update camera resolution config
2020-12-05 Create Setup folder
    Copies files over from Eugene's Github Raspberry Pi and software setup
2021-02-08 Copy version
    [incubator_pcb.kicad_pcb, incubator_pcb.sch, pi_zero_w.csv]
2021-02-21 Partial version with GPIO expander too.
    [channel_pair.sch, i2c_peripherals.sch, incubator_pcb.kicad_pcb, incubator_pcb.sch]
2021-02-27 PiOnlyPCB 202102: Routed again without I2C expanders, before IN* nets routed.
    [channel_pair.sch, i2c_peripherals.sch, incubator_pcb.kicad_pcb]
2021-02-27 Routed signals
    [incubator_pcb.kicad_pcb]
2021-02-28 PCB Ready to order. Passed DRC.
    [channel_pair.sch, incubator_pcb.kicad_pcb, incubator_pcb.sch]
2021-03-01 Update basic_all.py
    Update CAMERA_FREQ_SECONDS even if lights are off. Only take picture if lights are on.
2021-03-02 v202102 sent out to fab.
    [incubator_pcb-B_Cu.gbr, incubator_pcb-B_Mask.gbr, incubator_pcb-B_Paste.gbr, incubator_pcb-B_SilkS.gbr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]
2021-03-13 Render PCB for upload.
2022-10-29 Rename PiOnlyPCB as v3 to improve discoverability
    [channel_pair.sch, i2c_peripherals.sch, incubator_pcb-B_Cu.gbr, incubator_pcb-B_Mask.gbr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]
2022-10-29 Import mainboard style v4 PCB from 2022-02-20.
    [op_mainboard1-B_Cu.gbl, op_mainboard1-B_Mask.gbs, op_mainboard1-B_Paste.gbp, op_mainboard1-B_Silkscreen.gbo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]
2026-01-04 checking in all files for the esp32 incubator
    [ATX_Connector_24pi_90deg.stp, Incubator-PowerBoard-B_Cu.gbl, Incubator-PowerBoard-B_Fab.gbr, Incubator-PowerBoard-B_Mask.gbs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]
2026-01-04 moved old designs into archive directory. renamed new control board directory
    [ATX_Connector_24pi_90deg.stp, Incubator-PowerBoard-B_Cu.gbl, Incubator-PowerBoard-B_Fab.gbr, Incubator-PowerBoard-B_Mask.gbs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]
